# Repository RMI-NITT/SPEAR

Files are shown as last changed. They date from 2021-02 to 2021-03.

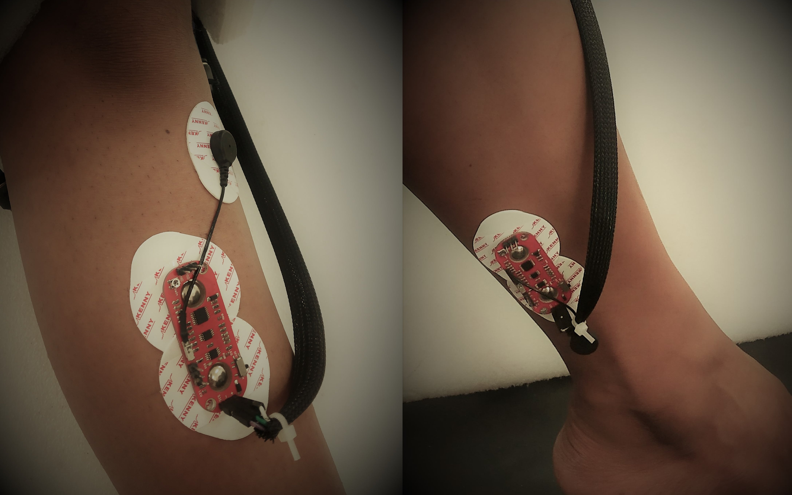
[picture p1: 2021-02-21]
ICC 2019/Latex Pics/Electrodes.jpg

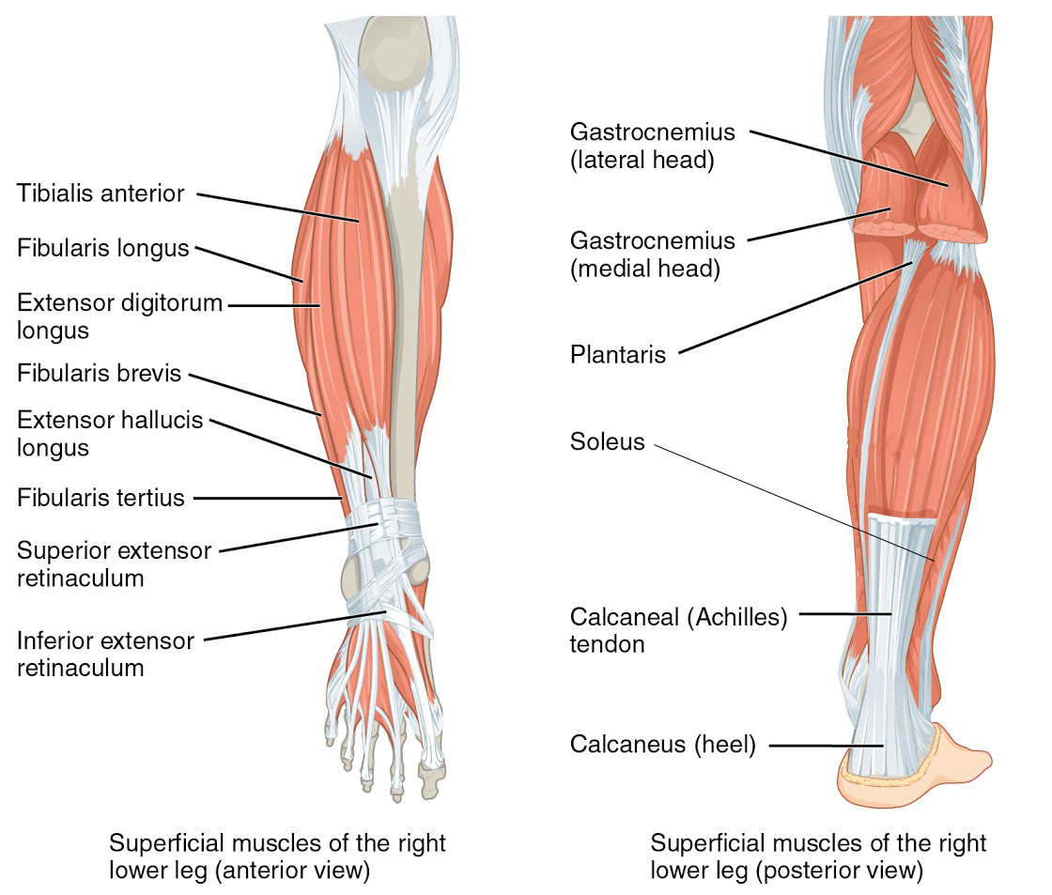
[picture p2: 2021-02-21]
ICC 2019/Latex Pics/Muscles.jpg

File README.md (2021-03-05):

# SPEAR - Soft Pneumatic EMG Assisted Rehabilitation

<p align=justify> SPEAR is an Active Ankle-Foot Orthosis (AFO), aimed at providing an affordable solution for rehabilitating foot drop of stroke survivors.</p>

<p align=justify> Stroke patients often suffer from foot drop, a gait abnormality usually due to the paralysis of the anterior portion muscles of the lower leg, causing an inability or impaired ability to raise the foot at the ankle joint. This leads to extremities of the foot being dragged along the ground while walking, causing tripping and other accidents. Braces or splints that fit into shoes are prescribed to help hold the foot in a normal position. For rehabilitation, most patients are trained to walk with canes, and therapists prescribe physiotherapy for a series of short, intensive sessions. These solutions are expensive and slow processes as they require the presence of skilled personnel and are carried out for short durations.</p>

<p align=justify> The AFO is designed to rehabilitate the foot by augmenting the human musculoskeletal system. It is actuated using McKibben Muscles (Pneumatic Artificial Muscles), which are driven pneumatically. They are cost-effective, lightweight and compliant, offering a significant advantage over Motor Driven orthoses. The orthosis is controlled using Electromyography(EMG) signals from the muscles involved in the motion of the ankle. The EMG sensors are non-invasive, and all computation and control required for the operation of the orthosis run onboard the orthosis in real time.</p>

## Videos
<a href="https://www.youtube.com/watch?v=0MvOgEBvByQ&list=PL44ElmNkyTvBkK0XeyDZ0ApXayw_p0Ibq&index=23">SPEAR Introduction</a>
<br>
<a href="https://www.youtube.com/watch?v=0MvOgEBvByQ&list=PL44ElmNkyTvBkK0XeyDZ0ApXayw_p0Ibq&index=24">SPEAR Working Video</a>
<br>
<a href="https://www.youtube.com/watch?v=SkU-yHnwb48&list=PL44ElmNkyTvCRuWAIcXDtp5S97rujg1kM&index=5">SPEAR Graphical Interface</a>
<br>
<a href="https://www.youtube.com/watch?v=TKFv4CyoDiE&list=PL44ElmNkyTvCRuWAIcXDtp5S97rujg1kM&index=6">SPEAR Project Display</a>

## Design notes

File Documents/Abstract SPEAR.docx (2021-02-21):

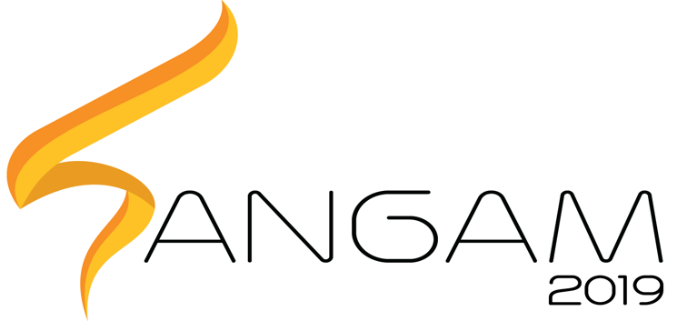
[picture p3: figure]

PRAGYAN HARDWARE HACKATHON

Healthcare and Life Sciences

SPEAR

Soft Pneumatic Electromyographically Assisted Rehabilitation

Name College ID/Roll UG/PG Course/Branch Semester

Name | Roll Number | UG/PG | Branch | Semester
Nitish Gudapati | 111117036 | UG | Mech | III
Koushik Kumaran | 108117056 | UG | ECE | III
Jinesh R | 107117045 | UG | EEE | III
Deepak S V | 107117033 | UG | EEE | III
Himadri Poddar | 110117035 | UG | ICE | III
Mukesh Kanna | 111117070 | UG | Mech | III

1. Project Abstract:

Stroke patients often suffer from Foot Drop, a paralysis of the muscles in the anterior portion of the lower leg, causing an inability or impaired ability to raise the foot from the ankle. This leads to extremities of the foot dragging along the ground while walking, and can cause tripping and other accidents. Presently, patients are trained to walk with canes, and physiotherapy is also prescribed. The physiotherapy requires the presence of a trainer, and these frequent consultations lead to huge expenditure.

Currently, robotic therapeutic tools exist, but the rigidity does not lend itself to the compliant nature of the body, and are unwieldy. They are bulky and heavy which makes them unwearable under regular usage.

As a bio-inspired solution, SPEAR aims to provide a soft robotic approach to the physio therapy. The end effectors at the ankle are a set of soft pneumatic actuators, controlled by electromyographic signals (EMG). This achieves a reduction of weight at the joint, and can be custom made to fit the patient’s needs.

Keywords — Rehabilitative robotics, stroke, foot drop, Soft robotics, soft pneumatic actuators, Electromyography

2. Proposed Design:
A. Objective:

The objective is to rehabilitate patients with foot drop by fabricating a set of soft robotic actuators mimicking the muscle-skeleton system, controlled via electromyography (EMG) signals.

B. Proposed Solution:
  a. Block Diagram:

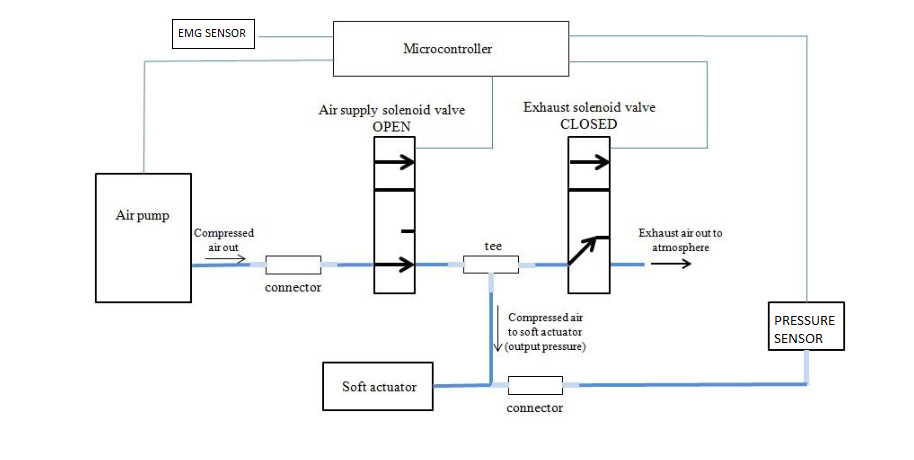
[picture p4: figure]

C. Components Required:

COMPONENTS/PARTS | How is it being used in the proposed solution? Explain its role/functionality.
Thermoplastic Polyurethane / Silicone rubber tube, Nylon Mesh | Fabricate the pneumatic actuator
Air compressor | To compress the air from atmosphere and transfer the compressed air to pneumatic actuators
Solenoid Valve | To control the air flow to pneumatic actuators
MCU | To control the solenoid valve from the data obtained from the corresponding EMG sensors
Electromyographic (EMG) sensor | To measure the electrical activity of muscles

3. Innovativeness of the Proposed Solution

Compared to other rehabilitative robots, a soft robot will be lighter, smaller and wearable. The soft nature of the robot, makes it more compliant with the human body, giving a great increase in comfort over existing solutions. The weight is also much less than that of a rigid structure, reducing the load on the ankle.

Electromyograph signals (EMG) eliminates the need for manual control, and makes the robot feel like a natural extension of the human body.

Compared to traditional therapeutic methods, the cost will be greatly decreased due to the one-time investment.

4. Impact of the proposed solution (Application):

Ease of physiotherapy for those affected with stroke. Physiotherapy is a costly and continuous process, whereas a robotics solution will be a one-time investment. Because of its compliant nature, SPEAR is lighter, smaller and easier to use, contrary to traditional rigid approaches.

5. References

https://softroboticstoolkit.com

https://hpac.harvard.rdu/softrobotics

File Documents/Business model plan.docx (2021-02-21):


PRAGYAN HARDWARE HACKATHON

SPEAR – Soft Pneumatic Electromyography (EMG)

Assisted Rehabilitation

- Key resources: Intellectual: Any patents etc that arise from SPEAR.
- Value propositions: SPEAR offers its customers cost effective, one-time investment solution rather than conventional physiotherapy process which consumes both money and time to a large extent.
- Cost structure:

Orthosis - 6000

EMG Sensors - 5000

McKibben muscles - 400

Compressor and Tank - 1600

Pneumatic Valves - 2500

Miscellaneous (Tubes, connectors, etc.) - 500

Total - 16000

- Future work: Since it is a niche product, SPEAR requires the funding and support of a major healthcare corporation to survive. We plan to present perfect the design and approach specialists from the healthcare industry to acquire funding for production, marketing and distribution of SPEAR.

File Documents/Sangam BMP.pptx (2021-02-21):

## SPEAR Soft Pneumatic EMG Assisted Rehabilitation

Gudapati Nitish
Koushik Kumaran
Mukesh Kanna
Jinesh R
Deepak SV
Himadri Poddar

## Objective:

- The primary objective of SPEAR is to provide a cheap and affordable soft AFO(Ankle-Foot Orthosis) for easy use by patients and reduction of therapy costs.
- SPEAR is designed to be safe due to the use of soft McKibben actuators, eliminating the possibility of injury that is present with any rigid apparatus due to unexpected movement.

## Work Plan:

MONTH | Work completed
December | Actuator Fabrication and testing
January | EMG Signal Processing
February | Orthosis and Tank fabrication
March | Integration of all modules

## Status:

- The orthosis has been fully fabricated with two degrees of freedom (Dorsiflexion and Plantarflexion).
- EMG signal processing has been completed, and user intent has been established.
- A compressor has been fitted with an air tank to provide pressurized air to the orthosis.
- The above three modules have been integrated to give a complete working model.

## Future Work:

The Orthosis can be extended to Inversion and Eversion motion in the ankle.
The Orthosis which has primarily been optimised for rehabilitation can be upgraded to Exoskeleton for the lower limb.
Expandability is present for machine learning algorithms for greater accuracy of EMG intent estimation.
The main features of this exoskeleton:
1. Soft McKibben muscles provide actuation, eliminating rigidity and preventing damage to the user
2. Autonomous control of the Lower limb with Electromyography signals.

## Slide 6

Business Model Plan:

Key Partners Healthcare and Pharmaceutical companies | Key Activities Creation of efficient Supply Chain, Creation of a cheap channel to acquire raw materials. | Value Propositions SPEAR offers its customers cost effective, one-time investment solution rather than conventional physiotherapy process which consumes both money and time to a large extent. | Customer Relationship Dedicated Personal Assistance | Customer Segments Niche market: Patients with foot drop(primarily stroke patients)
| | | Channels Healthcare companies to spread word of mouth to specialists, who can recommend SPEAR to patients
| Key Resources: Intellectual: Any patents, etc. that arise from SPEAR.

Cost Structure: Orthosis- 6000 EMG Sensors - 5000 McKibben muscles – 400 Compressor and Tank – 1600 Pneumatic Valves - 2500 Miscellaneous(Tubes, connectors, etc.) – 500 Total – 16000 | Revenue Streams Funding from Healthcare and Pharmaceutical Companies, Hospitals. Sales Profits

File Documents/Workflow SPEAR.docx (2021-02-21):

S.P.E.A.R Workflow

January:

Week 1:

Fabricator testing

Week 2:

Prototype creation and testing

Week 3:

Pneumatic circuit fabrication, EMG sensor acquisition

Week 4:

Control of Mechanism with hard coded angles, EMG signal processing

February:

Week 1:

EMG signal processing, start of fabrication of orthosis for inversion, eversion

Week 2:

EMG signal processing, completion of orthosis

Week 3:

Completion of EMG signal processing, integration of EMG results with completed orthosis

Week 4:

Testing and refinement

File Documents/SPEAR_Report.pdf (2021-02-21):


## PRAGYAN HARDWARE HACKATHON

## Healthcare and Life Sciences

## SPEAR

## Soft Pneumatic Electromyographically Assisted Rehabilitation

Name | College ID/Roll UG/PG | Course/Branch Semester
Name | Roll Number | UG/PG | Branch | Semester
Nitish Gudapati | 111117036 | UG | Mech | III
Koushik Kumaran | 108117056 | UG | ECE | III
Jinesh R | 107117045 | UG | EEE | III
Deepak S V | 107117033 | UG | EEE | III
Himadri Poddar | 110117035 | UG | ICE | III
Mukesh Kanna | 111117070 | UG | Mech | III

### 1. Project Abstract:

Stroke patients often suffer from Foot Drop, a paralysis of the muscles in the anterior portion of the lower leg, causing an inability or impaired ability to raise the foot from the ankle. This leads to extremities of the foot dragging along the ground while walking, and can cause tripping and other accidents. Presently, patients are trained to walk with canes, and physiotherapy is also prescribed. The physiotherapy requires the presence of a trainer, and these frequent consultations lead to huge expenditure.
Currently, robotic therapeutic tools exist, but the rigidity does not lend itself to the compliant nature of the body, and are unwieldy. They are bulky and heavy which makes them unwearable under regular usage.
As a bio-inspired solution, SPEAR aims to provide a soft robotic approach to the physio therapy. The end effectors at the ankle are a set of soft pneumatic actuators, controlled by electromyographic signals (EMG). This achieves a reduction of weight at the joint, and can be custom made to fit the patient’s needs.

Keywords — Rehabilitative robotics, stroke, foot drop, Soft robotics, soft pneumatic actuators, Electromyography

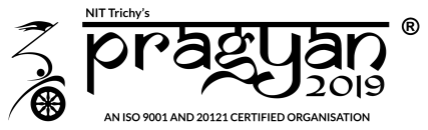
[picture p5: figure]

### 2. Proposed Design:

A. Objective:

The objective is to rehabilitate patients with foot drop by fabricating a set of soft robotic actuators mimicking the muscle-skeleton system, controlled via electromyography (EMG) signals.

B. Proposed Solution:
a. Block Diagram:

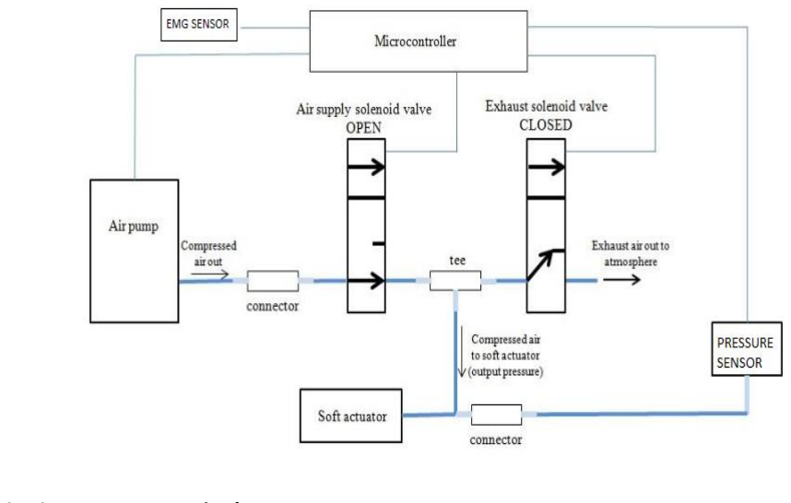
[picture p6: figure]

C. Components Required:
COMPONENTS/PARTS | How is it being used in the proposed solution? Explain its role/functionality.
Thermoplastic Polyurethane / Silicone rubber tube, Nylon Mesh | Fabricate the pneumatic actuator
Air compressor | To compress the air from atmosphere and transfer the compressed air to pneumatic actuators
Solenoid Valve | To control the air flow to pneumatic actuators
MCU | To control the solenoid valve from the data obtained from the corresponding EMG sensors
Electromyographic (EMG) sensor | To measure the electrical activity of muscles

### 3. Innovativeness of the Proposed Solution

Compared to other rehabilitative robots, a soft robot will be lighter, smaller and wearable. The soft nature of the robot, makes it more compliant with the human body, giving a great increase in comfort over existing solutions. The weight is also much less than that of a rigid structure, reducing the load on the ankle.
Electromyograph signals (EMG) eliminates the need for manual control, and makes the robot feel like a natural extension of the human body.
Compared to traditional therapeutic methods, the cost will be greatly decreased due to the one-time investment.

### 4. Impact of the proposed solution (Application):

Ease of physiotherapy for those affected with stroke. Physiotherapy is a costly and continuous process, whereas a robotics solution will be a one-time investment. Because of its compliant nature, SPEAR is lighter, smaller and easier to use, contrary to traditional rigid approaches.

### 5. References

https://softroboticstoolkit.com

https://hpac.harvard.rdu/softrobotics

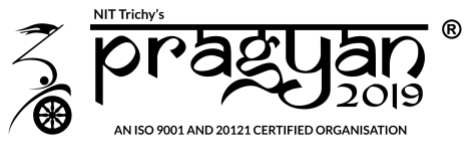
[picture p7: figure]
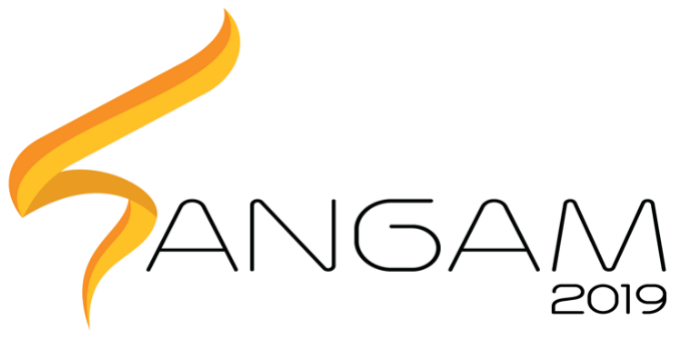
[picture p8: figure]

# Healthcare and Medical Sciences

# S.P.E.A.R

# Soft Pneumatic EMG Assisted Rehabilitation

## PRAGYAN HARDWARE HACKATHON

# Aim

# The objective of S.P.E.A.R is to provide an affordable soft robotic ankle foot orthosis for rehabilitative purposes, aimed primarily

at stroke survivors.

# Application

# Ease of physiotherapy for those affected with stroke. Physiotherapy is a costly and continuous process, whereas a robotics solution will be a one-time investment. Because of its compliant nature, SPEAR is lighter, smaller and easier to use, contrary to traditional rigid

approaches.

# ANKLE MOTION

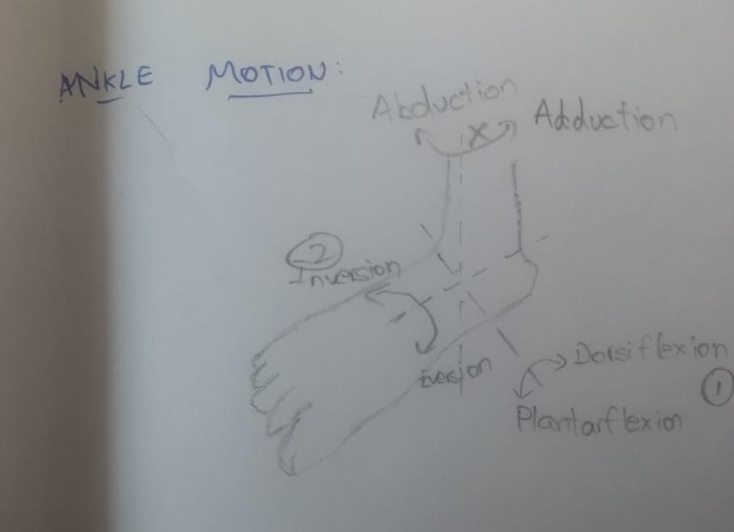
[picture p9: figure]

# Block Diagram

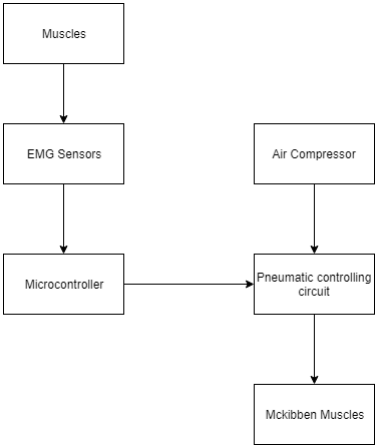
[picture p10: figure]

# Progress Report

# - McKibben Muscles

have been fabricated.

# - The price of a readymade McKibben muscle is minimum

Rs.1500

# - Using off-the shelf components, cost has been reduced to an

average Rs.150,

# depending on Muscle size, diameter

Component | Cost(Rs.)
Bladder(Silicon Rubber) | 40 - 60
Nylon Mesh Sleeve | 40 - 60
Miscellaneous (Connectors, Seals) | 50
Total | 150

# Testing Results

Inner Diameter (inch) | Outer Diameter (inch) | Length (cm) | Slack | Contraction (cm) | Percentage Contraction
1/3 | 1/2 | 20 | No | 2.5 | 12.5
1/3 | 1/2 | 20 | Yes | 0.5 | 2.5
1/2 | 5/8 | 30 | No | 3 | 10

# Muscle Test

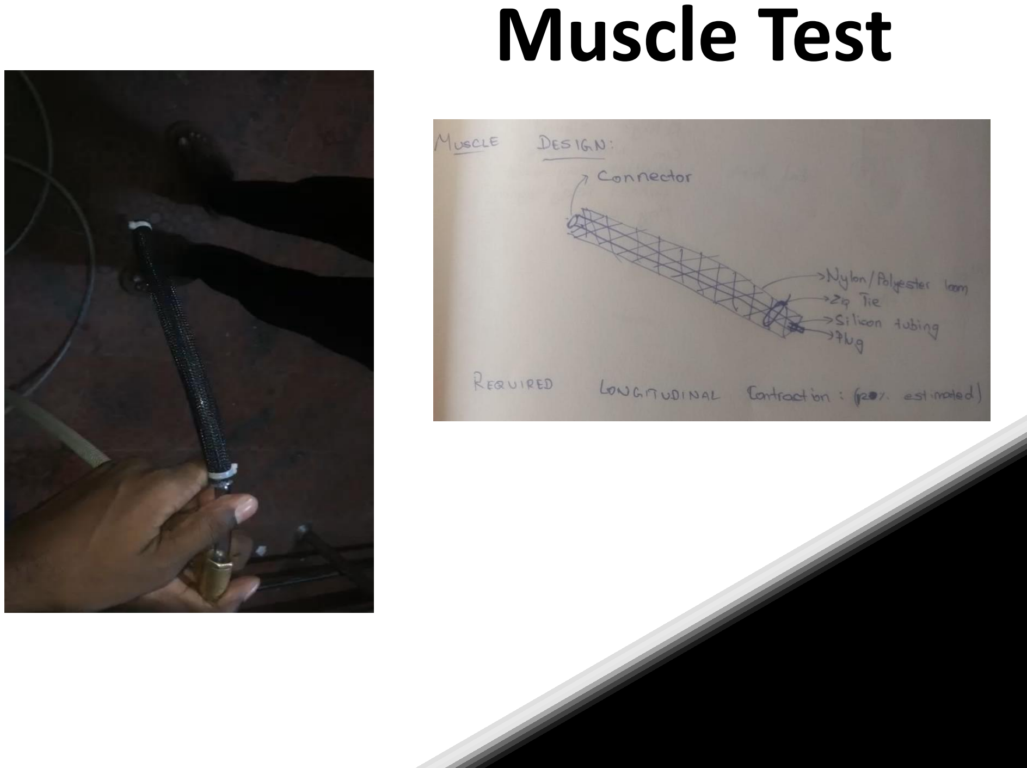
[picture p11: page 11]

# First Prototype

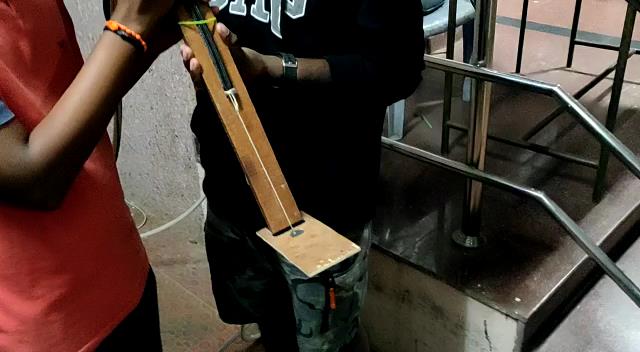
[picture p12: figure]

# Dorsiflexio

n

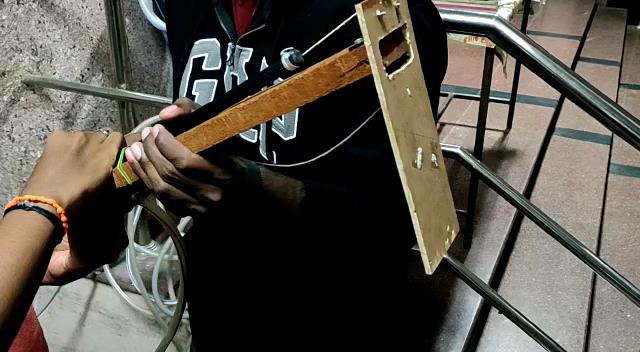
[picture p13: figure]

# Plantarflexion

# Second Prototype (120˚ range of motion)

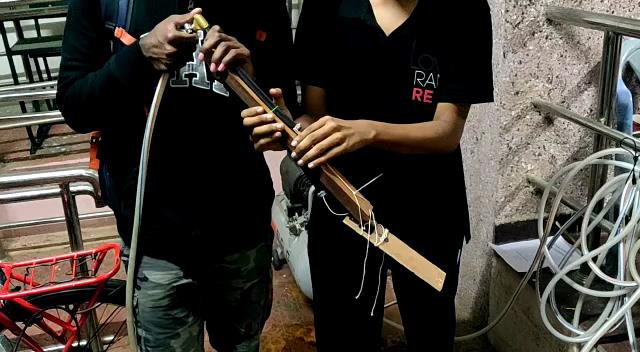
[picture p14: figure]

# Dorsiflexio

n

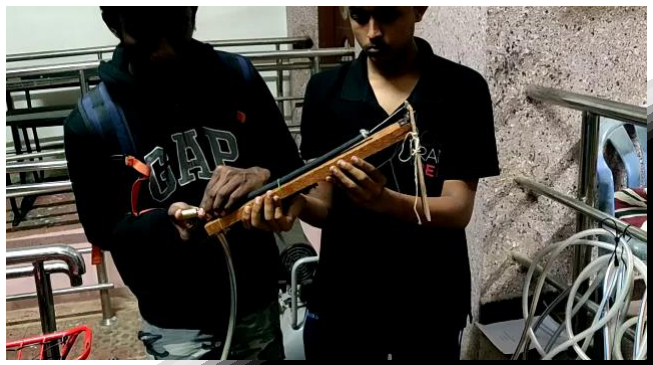
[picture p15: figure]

# Plantarflexion

S.P.E.A.R Workflow

January:

Week 1:

Fabricator testing

Week 2:

Prototype creation and testing

Week 3:

Pneumatic circuit fabrication, EMG sensor acquisition

Week 4:

Control of Mechanism with hard coded angles, EMG signal processing
February:

Week 1:

EMG signal processing, start of fabrication of orthosis for inversion, eversion

Week 2:

EMG signal processing, completion of orthosis

Week 3:

Completion of EMG signal processing, integration of EMG results with completed orthosis

Week 4:

Testing and refinement

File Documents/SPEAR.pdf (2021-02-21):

# S.P.E.A.R

# Soft Pneumatic EMG Assisted Rehabilitation

# Aim

# SPEAR is an Active

Ankle-Foot Orthosis (AFO),

# aimed at providing a cheap and affordable solution for rehabilitating stroke

survivors.

# Abstract

- Stroke patients often suffer from Foot Drop, a paralysis of the muscles in the anterior portion of the lower leg, causing an inability or impaired ability to raise the foot from the ankle. This leads to extremities of the foot dragging along the ground while walking, and can cause tripping and other accidents. Presently, patients are trained to walk with canes, and physiotherapy is also prescribed. The physiotherapy requires the presence of a trainer, and these frequent consultations lead to huge expenditure.
- Currently, robotic therapeutic tools exist, but the rigidity does not lend itself to the compliant nature of the body, and are unwieldy. They are bulky and heavy which makes them unwearable under regular usage.
- As a bio-inspired solution, SPEAR aims to provide a soft robotic approach to the physio therapy. The end effectors at the ankle are a set of soft pneumatic actuators, controlled by electromyography signals (EMG). This achieves a reduction of weight at the joint, and can be custom made to fit the patient’s needs.
- Keywords — Rehabilitative robotics, stroke, foot drop,
Soft | robotics, | soft | pneumatic | actuators,
Electromyography

# Application

## Ease of physiotherapy for those affected with stroke. Physiotherapy is a costly and continuous process, whereas a robotic solution would be a one-time investment. Because of its compliant nature, SPEAR is lighter, smaller and easier to use, contrary to traditional

rigid approaches.

COMPONENTS / PART | Role / Functionality.
Thermoplastic Polyurethane, Nylon Mesh | Fabricate the pneumatic actuator
Air compressor | To compress the air from atmosphere and transfer the compressed air to pneumatic actuators
SolenoidValve | To control the air flow to pneumatic actuators
MCU | To control the solenoid valve from the data obtained from the corresponding EMG sensors
Electromyographic (EMG) sensor | To measure the electrical activity of muscles

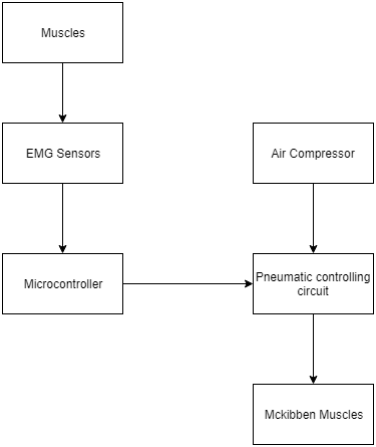
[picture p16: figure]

# Block Diagram

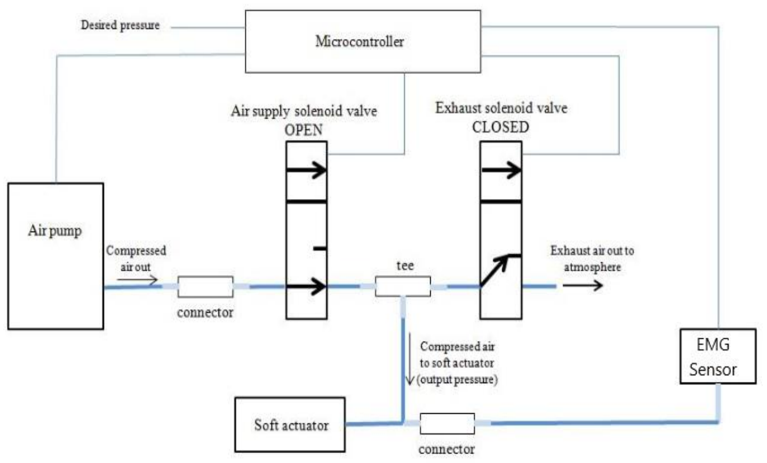
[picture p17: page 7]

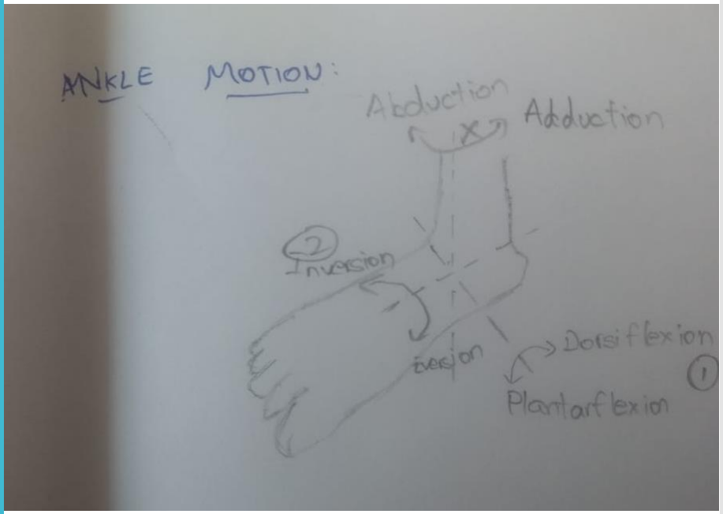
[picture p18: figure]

# Ankle Motion

# McKibben Muscles

## (Soft artificial muscles)

- McKibben Muscles
have been
fabricated.
- The price of a
readymade
McKibben muscle
is minimum
Rs.1500
- Using off-the shelf
components, cost
has been reduced
to an average
Rs.150, depending
on Muscle size,
diameter
Component | Cost(Rs.)
Bladder(Silicon Rubber) | 40 - 60
Nylon Mesh Sleeve | 40 - 60
Miscellaneous (Connectors, Seals) | 50
Total | 150

# Testing Results

Inner Diameter (inch) | Outer Diamete r (inch) | Length (cm) | Slack in Nylon Weave | Contrac tion (cm) | Percent age Contrac tion
1/3 | 1/2 | 20 | No | 2.5 | 12.5
1/3 | 1/2 | 20 | Yes | 0.5 | 2.5
1/2 | 5/8 | 30 | No | 3 | 10

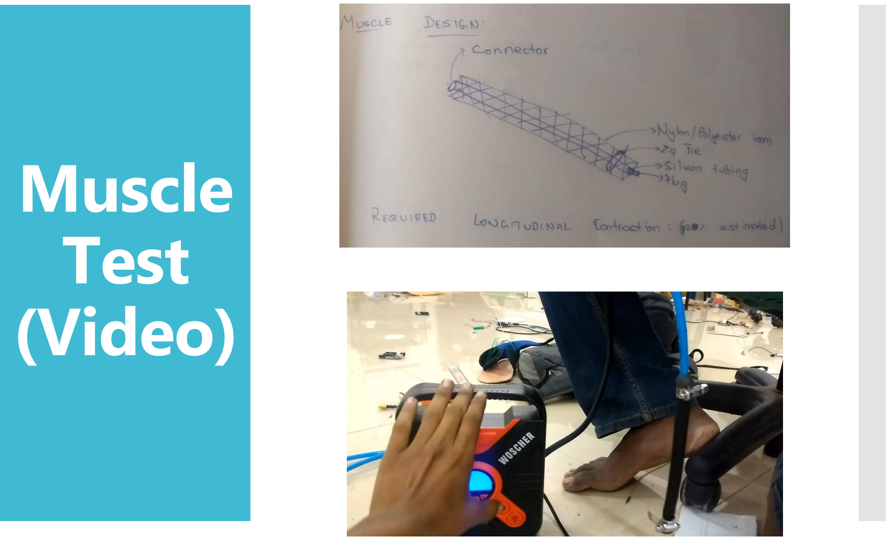
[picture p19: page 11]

# Muscle Test (Video)

# Prototype

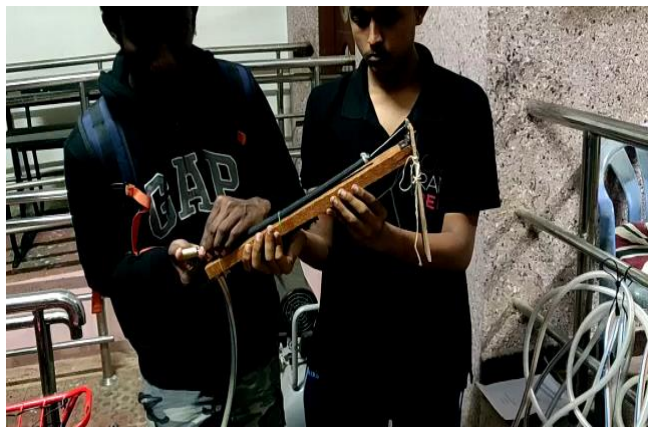
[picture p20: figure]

# (120˚ range of motion)


## Dorsiflexion

## Plantarflexion

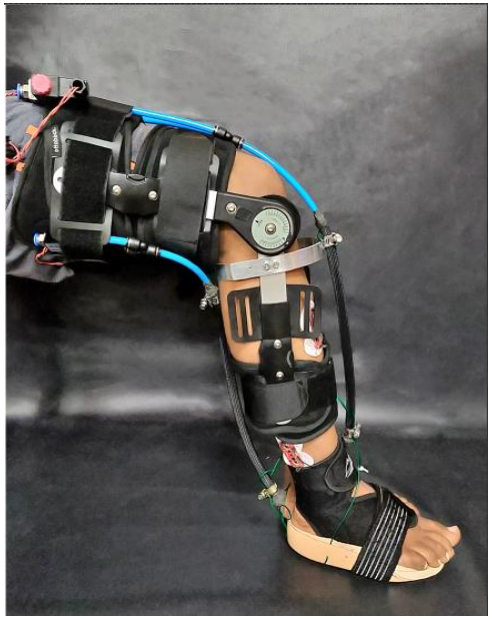
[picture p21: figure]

# Orthosis Design

# EMG Dynamic Thresholding (Video)

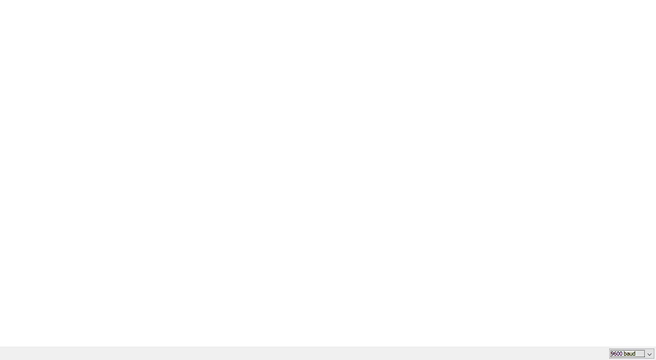
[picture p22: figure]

Tibialis Anterior
for Dorsiflexion

# EMG Voltage-Time Graph

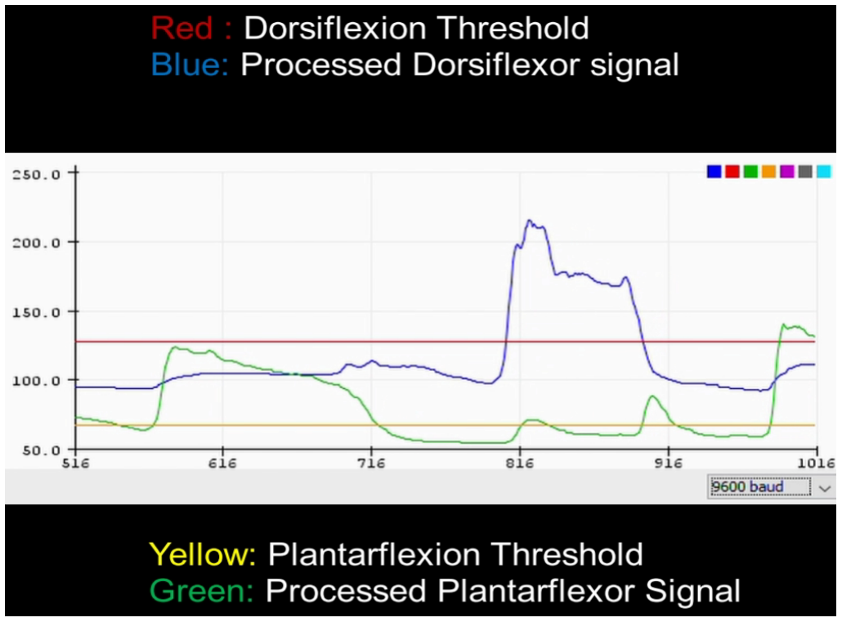
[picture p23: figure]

- Figure shows the voltage time graph obtained after the application of the Kalman Filter to both signals, and the threshold lines calculated using the above formula.

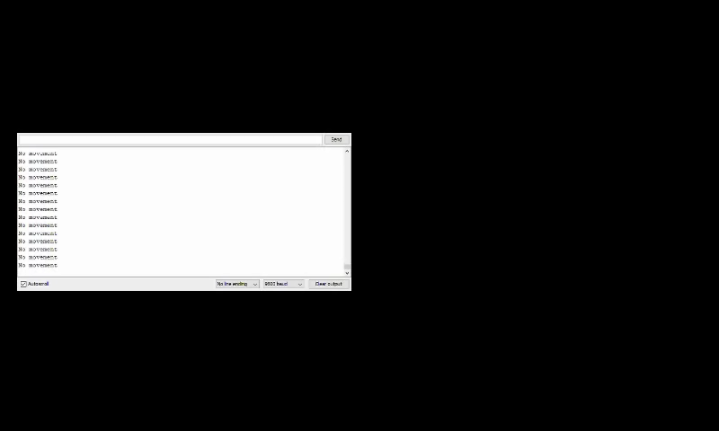
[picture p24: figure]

# EMG Intent Estimation (Video)

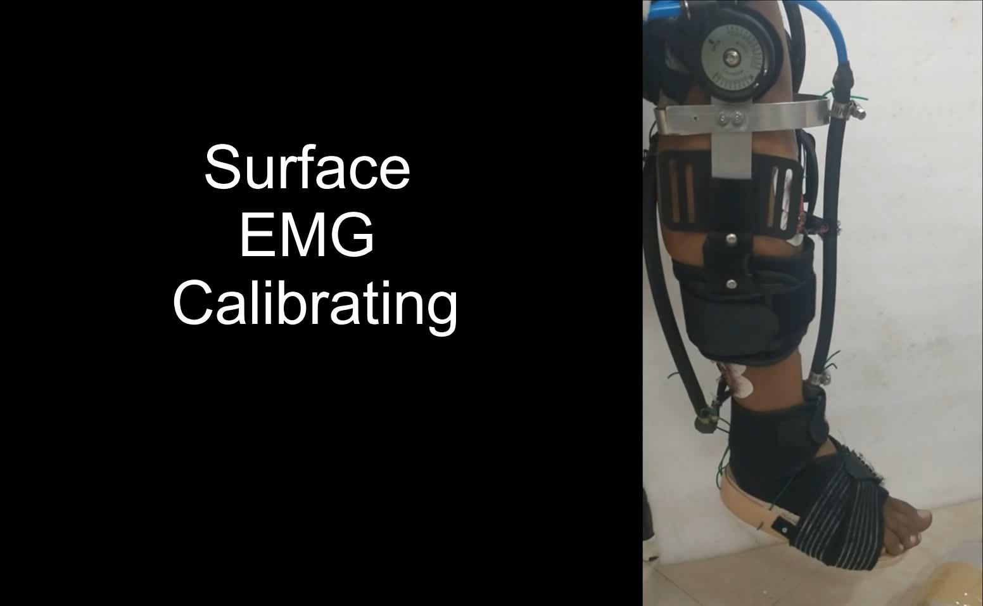
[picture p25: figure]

# Working Video

# Future Work

The Orthosis can be extended to Inversion and Eversion motion in the ankle.
The Orthosis which has primarily been optimised for rehabilitation can be upgraded to Exoskeleton for the lower limb.
Expandability is present for machine learning algorithms for greater accuracy of EMG intent estimation.
The main features of this exoskeleton:
1. Soft McKibben muscles provide actuation, eliminating rigidity and preventing damage to the user
2. Autonomous control of the Lower limb with Electromyography signals.

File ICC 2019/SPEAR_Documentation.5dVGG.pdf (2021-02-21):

## Design and Control of a Low-cost EMG-based Soft Robotic Ankle-Foot Orthosis for Foot Drop Rehabilitation*

Nitish Gudapati¹

, Koushik Kumaran²

, Deepak S V³

, Mukesh Kanna R⁴

, Jinesh R⁵
, Himadri Poddar⁶

Abstract— Stroke patients often suffer from foot drop, a gait abnormality usually due to the paralysis of the anterior portion muscles of the lower leg, causing an inability or impaired ability to raise the foot at the ankle joint. This leads to extremities of the foot being dragged along the ground while walking, causing tripping and other accidents. Braces or splints that fit into shoes are prescribed to help hold the foot in a normal position. For rehabilitation, most patients are trained to walk with canes, and therapists prescribe physiotherapy for a series of short, intensive sessions. These solutions are expensive and slow processes as they require the presence of skilled personnel and are carried out for short durations. In this paper, we present a novel design and control methodology for a 1-DoF Soft Active Ankle-Foot Orthosis (AFO) to address these issues. The AFO is designed to augment the human musculoskeletal system. The AFO is actuated using McKibben Muscles (Pneumatic Artificial Muscles), which are driven pneumatically. They are cost-effective and lightweight, offering a significant advantage over Motor Driven orthoses. The orthosis is controlled using Electromyography(EMG) signals from the muscles involved in the motion of the ankle. The use of EMG signals for control is found to be a better option than existing methods due to its non-invasive nature. It is also found to be simple and cost-effective for intent detection.

Keywords: Active-Foot-Orthosis, Electromyography (EMG), Foot Drop, Rehabilitation, Soft Robotics

I. INTRODUCTION
According to the World Health Organization, 15 million people suffer stroke worldwide each year. Of these, 5 million people die, and another 5 million are permanently disabled [1]. A common ailment for stroke survivors is foot drop, i.e., the inability to actively perform Dorsiflexion the foot. This leads to the occurrence of steppage gait, where the foot drags

*This work was supported by Institute grants through the Robotics and Machine Intelligence Club, NIT Tiruchirappalli, INDIA.
1Nitish Gudapati is a student at the Department of Mechanical Engineering, National Institute of Technology - Tiruchirappalli, Tiruchirappalli, Tamil Nadu 620015, INDIA gudapatinitish9@gmail.com 2Koushik Kumaran is a student at the Department of Electronics and Communication Engineering, National Institute of Technology - Tiruchirappalli, Tiruchirappalli, Tamil Nadu 620015, INDIA koushikkumaran52@gmail.com
3Deepak S V is a student at the Department of Electrical and Electronics Engineering, National Institute of Technology - Tiruchirappalli, Tiruchirappalli, Tamil Nadu 620015, INDIA svdeepak99@gmail.com 4Mukesh Kanna R is a student at the Department of Mechanical Engineering, National Institute of Technology - Tiruchirappalli, Tiruchirappalli, Tamil Nadu 620015, INDIA kanna.r1999@gmail.com
5
Jinesh R S is a student at the Department of Electrical and Electronics Engineering, National Institute of Technology - Tiruchirappalli, Tiruchirappalli, Tamil Nadu 620015, INDIA jineshrs2398@gmail.com 6Himadri Poddar is a student at the Department of Instrumentation and Control Engineering, National Institute of Technology - Tiruchirappalli, Tiruchirappalli, Tamil Nadu 620015, INDIA himadripoddar.nitt@gmail.com

along, requiring the patient to raise their knee higher than usual in the swing phase to counter this [2]. The patient’s foot slaps the ground during the foot strike phase of the gait cycle. Studies have shown that the entire kinematic chain of the lower body is disturbed, resulting in the functioning of the motor system under abnormal load [3].
Patients generally undergo therapy to regain motor control, and the required recovery can take from months to years to complete as shown in Fig.1 [4]. The available number of medical professionals are far less than the requirement, and they may not be accessible to all those who need it [5]. To this end, robotic devices can significantly decrease the burden on therapists and caregivers and can be used to provide intensive task-oriented practice.

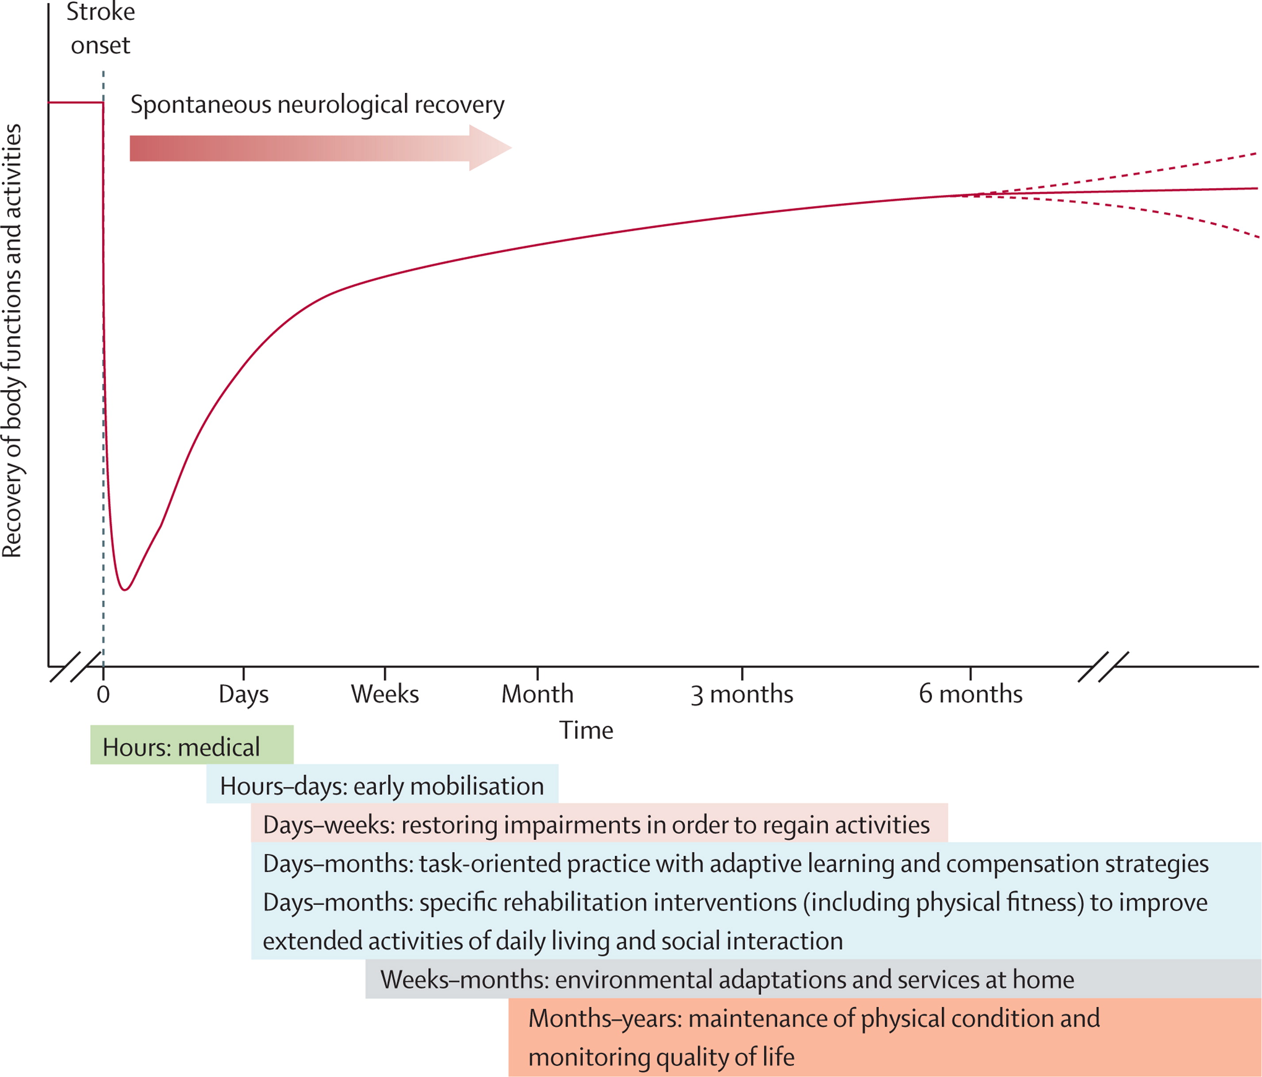
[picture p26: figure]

Fig. 1. A hypothetical pattern of recovery after stroke with the timing of intervention strategies Source: [4]

Considerable research has gone into developing such robotic devices, especially for upper-body rehabilitation [6]
[7] [8]. Most of these devices, however, are rigid, heavy and unwieldy. In recent years, the interest in a compliant robotic system has increased exponentially, due to the significant advantages they provide. Mckibben muscles or Pneumatic Artificial Muscles (PAM) are a possible actuation method with properties that make them uniquely suited for the application presented. These properties are explored in depth in Section IV.
In this paper, we describe the design and control of a single DOF orthosis, actuated with PAMs and controlled with Electromyography(EMG) Signals. The EMG sensors are non-invasive, and all computation and control required for the operation of the orthosis runs onboard the orthosis in real time. The design is compliant, lightweight and wearable. Section II explains the practices and techniques involved in the rehabilitation of the foot and section III explains the existing orthoses and exoskeletons for foot rehabilitation. Section IV discusses the construction and working of the prototype, and the results are presented in section V. Some concluding remarks and future scope is mentioned in section VI.

II. REHABILITATION TECHNIQUES

To understand the requirements and specifications of stroke rehabilitation devices, a brief introduction of existing techniques is given below [9].

A. Physiotherapy
The primary technique used is Physiotherapy which involves assessment of a Physiotherapist using various techniques. The techniques include various exercises.
1) Mobility training: To stabilise and strengthen to enhance balance and support.
2) Range of motion therapy: Helps in easing muscle tension allowing a good range of motion.
B. Technology-assisted
1) Functional electrical stimulation: This method involves inducing contraction to the weak muscles by application of electricity which helps in training them.
2) Game system technology: It is based on the idea of integration of games for rehabilitation. They involve functional activities and keep the patient occupied and motivated with games during the rehabilitation process.

III. EXISTING TECHNOLOGIES FOR REHABILITATION

Robotic exoskeletons have been employed in assisting individuals suffering from physical disability either for the advancement of therapy or as a permanent assistive tool. They are of various types, and can be classified based on their method of actuation:
- Rigid actuation: These devices are actuated using DC motors, Steppers etc.
- Soft actuation: These devices are actuated using compliant methods and are generally actuated pneumatically or using shape memory alloy (SMA) [10][13][14][15]. The AFO described in this paper falls under this category.
A. Rigid Actuation
1) Anklebot at Massachusetts Institute of Technology (MIT), USA: The Anklebot is a 3-DOF wearable robot, which is actuated by two linear screw actuators using two brushless dc motors. The linear actuators are mounted in parallel and provide actuation in two of the ankles 3-DOF, namely dorsiflexion-plantarflexion and inversioneversion [11]. Position information is provided by two sets of sensors: rotary encoders and linear encoders. No input is given by the user, and all movement is externally decided.
2) ALEX at University of Delaware, USA: This exoskeleton is mounted with a walker to support the device. The controller applies a force-field at the ankle of the subject. The linear actuators are mounted at the hip and knee of the orthosis. The torque generated by the actuators at these joints simulate the tangential forces needed to move the ankle of the subject along the trajectory [12]. The disadvantage is that it is not easily portable.
B. Soft Actuation
1) Wearable Soft Exoskeleton at Carnegie Mellon University, USA: The exoskeleton uses four PAMs placed on one of the lower legs (three anterior muscles for dorsiflexion, inversion, and eversion, and one posterior muscle for plantarflexion), which is connected to the knee brace and the foot brace with the help of artificial tendons. The artificial muscles were designed and placed as counterparts close to the biological muscles so that the device could provide additional forces to the corresponding muscles [13]. It is externally controlled using solenoid valves, and the sensors are used as position feedback for control without getting any input from the user. It helps with therapy, but it does not provide much independence for the user.
2) Powered ankle foot orthosis at University of Michigan, USA: This orthosis is actuated by PAMs providing only plantar flexion torque. It uses a real-time computer interface for controlling the air pressure supplied to the PAMs. The pressure is determined based on foot contact with the ground using a footswitch which is placed under the foot [14].
3) Adaptive control of actuated ankle foot orthosis (AAFO) at Paris-Est Crteil University, France: AAFO uses a predetermined trajectory of the ankles swing phase of the gait cycle, which helps in controlling the amount of assistance required for the ankle-foot orthosis. This method is employed as the current technologies are based on human/robot parameters, which are to be identified to set the magnitude of assistance required [15].

IV. CONSTRUCTION AND WORKING

A. Design of the Prototype

The design of the AFO focuses on achieving the following goals:
- User Comfort
- Minimal weight.
- Complete Range of Motion in a single axis.
- Simple setup.
- Minimal cost
1) Pneumatic Artificial Muscle Design: Each PAM consists of a silicone rubber tube, placed within a nylon mesh sleeve. The sleeve is kept in place with hose clamps on either end. One end is pneumatically sealed, and the other end is used as an inlet for pressurised air. Air is let in at around 40 psi. When air flows into the tube, it tends to expand volumetrically. The sleeves structure does not allow it to expand longitudinally, and rather, it expands radially while contracting longitudinally.

Multiple studies have been performed on these PAMs, and find the force-length characteristics to be similar to that of a muscle [16]. The materials used in the PAM are compliant, lightweight and low-cost. These properties make PAMs well suited for the AFO.

The required length and diameter of the PAMs were decided upon through experiments with various configurations, presented in Section V.


Fig. 2. AFOs Layout. Components labelled from (1) to (11): (1) Arduino Uno; (2) Motor drivers; (3) Solenoid Valves; (4) Li-Po; (5) Panel for electronic circuitry; (6) Knee braces; (7) PAM Mount; (8) PAM; (9) Foam padding; (10) Adjustable strings; (11) Orthotic Sole

2) Orthosis Design: The ground link of the Orthosis is located above the knee and functions and is connected to the second link around via a hinge joint. Another link is positioned on foot and acts as the end effector.

The brace and the sole are connected using two PAMs in an agonist-antagonist configuration, each one providing the necessary Dorsiflexion and Plantarflexion forces respectively. They can be modelled as slider mechanisms. The placement of the PAMs on the end is dependant on the required actuation torque and range of motion. Since PAMs are shown to provide a good amount of force [16], but only limited contraction, the choice was made to place them very close to the joint. This allows the AFO to achieve the entire Range of Motion which is roughly 20 degrees for dorsiflexion and 50 degrees for plantarflexion [17].

Some similar devices [18][19] have been constructed with the ground at the shin, connected to the ankle end effector in a similar fashion. We found that in this configuration, the transverse reaction forces during PAM contraction resulted in skin deformation at the skin-AFO interface. Such deformation was found to cause user discomfort and restrict the range of motion of the AFO. By placing the ground above the knee, the vector of reaction force is made almost completely normal to the skin-AFO interface as shown in Fig. 3.


Fig. 3. Interface between the skin and the orthosis


Fig. 4. Pneumatic Circuit

3) Electronics and Pneumatic Circuitry: Each PAM is controlled by a pair of 12V DC 2-Position 2-Way Solenoid Valves, where one acts as an inlet and the other acts as an outlet. Each pair of valves is connected to an L298N driver for logic. The drivers are connected to a Microcontroller Unit(MCU) (Arduino UNO). Two Myoware EMG sensors from Advancer Technologies are connected to the same MCU. The entire setup is powered by a 12V Lithium-Polymer Battery and placed on the ground link to optimise weight distribution throughout the AFO.
Both the inlet valves are connected to an air tank with pressurised air at 60psi, and the exhaust valves are left open to the atmosphere as shown in Fig.4. All pneumatic connections were made with 8 mm OD x 6 mm OD Polyurethane Pneumatic Tubes. The control methodologies for the PAMs are described in Section IV.B.4.
B. Control of the Orthosis
1) Signal Acquisition: In order to detect the intent of the user, the AFO uses EMG electrodes, connected to an MCU. Each McKibben muscle is placed so as to assist the functioning of a specific muscle. The targeted muscles are:
- Tibialis Anterior for Dorsiflexion
- Soleus for Plantarflexion
The positions of these muscles are depicted in Fig.5.
Each muscle requires a single non-invasive EMG sensor. Each sensor requires the placement of three electrodes to capture the differential component of the signal travelling across the muscle. As per EMG electrode placement standards [20], one electrode is placed near the centre of a muscle, one electrode near the end of a muscle and a ground electrode is placed near a bone for reference.


Fig. 5. Muscles of the leg Source: [21]

The rectified and integrated signal is passed from the signal pin of the sensor in the form of a 0 to 3.3V analog wave which is sampled by the 10-bit ADC of the MCU at a rate of 200Hz.


Fig. 6. Left: Electrode placement over the Tibialis Anterior Muscle; Right: Electrode placement over the Soleus Muscle

2) EMG Analysis: The rectified and integrated signals(signal envelopes) from the MyoWare muscle sensors were erratic and caused sudden spikes in the signal. To overcome this, the signals from both EMG sensors were passed to two independent 1-dimensional Kalman Filters, and the filtered output values of each iteration were taken as the estimated values for the next iteration. It was found that a Kalman Gain of 0.001 for both the filters gave the best results in removing noise from the signals, by inducing negligible latency in the filtered output as shown in Fig. 7. EMG signals for a muscle are highly dependant on a multitude of factors such as electrode placement, fatigue, and the physical and mental state of the user [22][23]. Hence, calibration is required before every session. This happens automatically on initialisation of the AFO. This calibration procedure sets the threshold for each muscle to enable intent estimation, which is described below.
The rest state characteristics of each muscle are obtained by recording the unfiltered EMG envelope for 10 seconds. The mean (µrest) and standard deviation (σrest) of this data


Fig. 7. EMG Signal Acquision, Filtering and Thresholding


Fig. 8. Intent Detection

are extracted from this data. Using the collected data, a threshold is calculated for each target muscle using (1) for Dorsiflexion and (2) for Plantarflexion. This threshold is then used to detect activation of each muscle. The muscle is found to be actively contracting when the filtered signal exceeds the threshold.
For Tibialis Anterior muscle, the threshold is determined by Eqn.1,
T = µrest +3σrest | (1)

For Soleus muscle, the threshold is determined by Eqn.2,

T = µrest +8σrest | (2)

Studies have shown that a threshold equal to the mean added to a multiple of the standard deviation gives good results when applied to the EMG envelope [24]. The values of the constant multiplier for standard deviation were determined experimentally, and the results of these tests are described in Section V.
3) Intent Detection Logic: Using the described method, it is possible to determine the state of a muscle in real time. Through experiments, it was found that the Soleus muscle was active during Plantarflexion and the initial, final stages of Dorsiflexion. This is visualized in Fig. 13, in which the patient performed Plantarflexion, followed by Dorsiflexion. Using this information, the User Intent can be detected by the method specified in Fig. 8

4) Control of PAM with EMG: The user closes the feedback loop by attempting to move their ankle by muscle contraction. This eliminates the need of external feedback, and allows real time intent detection.


Fig. 9. Operation Flowchart

In order to contract a PAM, pressurised air is inflated into it by opening the inlet valve and by closing the outlet valve. In order to relax (expand) a PAM, the air inside it is exhausted by closing the inlet valve and opening the outlet valve. The below table summarises the valve positions for different PAM configurations.

TABLE I

STATE OF SOLENOID VALVES

PAM movement | Inlet Valve | Exhaust Valve
Relax (Deflate) | Close | Open
Contract (Inflate) | Open | Close

In order to ensure smooth movement of the patients foot and avoid sudden movement, the speed of inflation/deflation of the PAMs was reduced by applying a Pulse Width Modulated(PWM) signal to the valves as shown in Fig. 10 and Fig.
11. Through experiments, it was found that a PWM signal with a time period of half a second and a duty cycle of 10% for 5 seconds was ideal.


Fig. 10. PWM Timing diagram during Inflation of the Muscle


Fig. 11. PWM Timing diagram during Exhaust of the Muscle

After detecting user intent, control signals from the MCU are sent to the pneumatic valves through the motor drivers. Table II describes the state of each PAM with respect to various user inputs.

TABLE II

STATE OF PNEUMATIC ARTIFICIAL MUSCLES

Intent | Dorsiflexor PAM | Plantarflexor PAM
Rest State | Relax | Relax
Plantarflexion | Relax | Contract
Dorsiflexion | Contract | Relax
V. RESULTS AND STATISTICAL DATA


Fig. 12. Prototype of the Ankle-Foot-Orthosis

A. Pneumatic Artificial Muscles Tests
The PAMs were tested by inflation at 35 psi with no external load to select the ideal contraction length required for the AFO.

TABLE III
PAM TESTS
Inner Diameter (inches) | Outer Diameter (inches) | Length of muscle (cm) | Length Contraction (cm) | Percentage Contraction (%)
1/3 | 1/2 | 20 | 2.5 | 12.5
1/2 | 5/8 | 20 | 1.8 | 9
1/3 | 1/2 | 30 | 5.1 | 17
1/2 | 5/8 | 30 | 3 | 10
B. EMG control Tests
The AFO was tested by three healthy individuals in two sessions each. The patients were asked to Flex their legs in a particular direction multiple times, and the percentage accuracy of intent detection was calculated.

TABLE IV

SESSION 1: SUBJECTS WERE WELL RESTED

Subject | Dorsiflexion Accuracy(%) | Plantarflexion accuracy(%)
1 | 95 | 95
2 | 100 | 90
3 | 95 | 90

TABLE V

SESSION 2: SUBJECTS WERE FATIGUED

Subject | Dorsiflexion Accuracy(%) | Plantarflexion accuracy(%)
1 | 95 | 90
2 | 90 | 90
3 | 90 | 90

From the above results, it is found that the simple control scheme presented is able to achieve a mean Dorsiflexion accuracy of 94.17%, and inaccuracies being 4.17% true-negative and 1.66% false-positive and. The mean Plantarflexion accuracy is 90.83% and the inaccuracies are 5.83% true-negative and 3.34% false-positive. It is worth noting that the accuracy decreases minimally when the patients are not wellrested. For well rested patients, the control scheme achieves a mean Dorsiflexor accuracy of 96.7% and inaccuracies being 1.65% false-positive and 1.65% true-negative. The mean Plantarflexion accuracy is 91.7% and the inaccuracies are 6.7% true-negative and 1.6% false-positive.


Fig. 13. Voltage-time graph obtained after the application of the Kalman Filter to both signals as well as the threshold lines

VI. CONCLUSIONS
The design and control of a 1 DOF Soft Ankle Foot Orthosis has been presented in this paper. The prototype shows promise to be as a therapeutic alternative. The AFO uses EMG signals which are reliable and easy to calibrate. The main purpose of the work is to replace the rigid and heavy hardware previously used for robotic rehabilitation. The AFO uses McKibben Muscles/PAMs, which are pneumatically actuated, low-cost and lightweight. The torque provided by the AFO can be increased by enhancing air pressure driving techniques, and this could allow the use of the device as a powered exoskeleton. Also, machine learning algorithms could be used to estimate the intent of the user with greater accuracy. The device could also be further developed by incorporating more degrees of freedom. This would allow the AFO to perform Inversion and Eversion of the leg.
| REFERENCES
[1] ”World Health Report” - 2002 from the World Health Organization Retrieved on: 10 May 2019 from http://www.who.int/whr/2002/en/.
[2] ”Walking abnormalities” MedlinePlus Retrieved on: 5 June 2019 from https://medlineplus.gov/ency/article/003199.htm
[3] Wiszomirska I, Bakiewicz M, Kaczmarczyk K, Brzuszkiewicz-Kumicka G, Wit A. Effect of Drop Foot on Spatiotemporal, Kinematic, and Kinetic Parameters during Gait. Appl Bionics Biomech. 2017;2017:3595461. doi:10.1155/2017/3595461.
[4] P. Langhorne, J. Bernhardt and G. Kwakkel, Stroke Rehabilitation, Stroke Care 2, The Lancet Vol 377, May 2011.
[5] K.X. Khor, H.A. Rahman, S.K. Fu et al. A Novel Hybrid Rehabilitation Robot for Upper and Lower Limbs Rehabilitation Training. Int. Conf. on Robot PRIDE (ConfPRIDE) 2013-2014, Procedia Computer Science 42 (2014) p. 293-300.
[6] A. Asokan and M. Vigneshwar, ”Design and Control of an EMG-based Low-cost Exoskeleton for Stroke Rehabilitation,” 2019 Fifth Indian Control Conference (ICC), New Delhi, India, 2019, pp. 478-483. doi: 10.1109/INDIANCC.2019.8715555
[7] Kim B, Deshpande AD. An Upper-Body Rehabilitation Exoskeleton Harmony with an Anatomical Shoulder Mechanism: Design, Modeling, Control, and Performance Evaluation. Int. Journal. of Robotics Research (IJRR) 2017, Vol 36 Issue 4, p. 414-435.
[8] J. C. Perry and J. Rosen.Design of a 7 Degree-of-Freedom Upper-Limb Powered Exoskeleton. The First IEEE/RAS-EMBS Int. Conf. on Biomedical Robotics and Biomechatronics, 2006. BioRob 2006., Pisa, 2006, pp. 805-810.
[9] | Stroke | rehabilitation: | What | to | expect | as | you | recover.
(May | 24, | 2017). | Retrieved | on | 2 | June | 2019, | from
https://www.mayoclinic.org/diseasesconditions/stroke/in-depth/strokerehabilitation/art-20045172
[10] K. Ikuta, ”Micro/miniature shape memory alloy actuator,” Proceedings., IEEE International Conference on Robotics and Automation, Cincinnati, OH, USA, 1990, pp. 2156-2161 vol.3. doi: 10.1109/ROBOT.1990.126323
[11] Roy, A., Krebs, H. I., Williams, D. J., Bever, C. T., Forrester, L. W., Macko, R. M., & Hogan, N. (2009). Robot-Aided Neurorehabilitation: A Novel Robot for Ankle Rehabilitation. IEEE Transactions on Robotics, 25(3), 569582. doi:10.1109/tro.2009.2019783
[12] Banala, S. K., Seok Hun Kim, Agrawal, S. K., & Scholz, J. P. (2009). Robot Assisted Gait Training With Active Leg Exoskeleton (ALEX). IEEE Transactions on Neural Systems and Rehabilitation Engineering, 17(1), 28.doi:10.1109/tnsre.2008.2008280
[13] Park, Y.-L., Chen, B., Prez-Arancibia, N. O., Young, D., Stirling, L., Wood, R. J., Nagpal, R. (2014). Design and control of a bio-inspired soft wearable robotic device for anklefoot rehabilitation. Bioinspiration & Biomimetics, 9(1), 016007.doi:10.1088/1748-3182/9/1/016007
[14] Gordon, K. E., Sawicki, G. S., & Ferris, D. P. (2006). Mechanical performance of artificial pneumatic muscles to power an anklefoot orthosis. Journal of Biomechanics, 39(10), 18321841.doi:10.1016/j.jbiomech.2005.05.018
[15] Arnez-Paniagua, V., Rifai, H., Amirat, Y., & Mohammed, S. (2017). Adaptive control of an actuated-ankle-foot-orthosis. 2017 International Conference on Rehabilitation Robotics (ICORR). doi:10.1109/icorr.2017.8009474
[16] Takosoglu, Jakub & Laski, P & Blasiak, Slawomir & Bracha, Gabriel & Pietrala, Dawid. (2016). Determining the Static Characteristics of Pneumatic Muscles. Measurement and Control. 49. 62-71. 10.1177/0020294016629176.
[17] ”Generally Accepted Values for Normal Range of Motion (ROM) in Joints” (May 14, 2019) Retrieved on 8 June 2019 from https://www.verywellhealth.com/what-is-normal-range-of-motion-ina-joint-3120361
[18] Ferris DP, Czerniecki JM, Hannaford B. An ankle-foot orthosis powered by artificial pneumatic muscles. J Appl Biomech. 2005;21(2):189197.
[19] Zhu, Y. (2017). Design and web-based control of a soft ankle foot orthosis. 17. 82-88.
[20] Datasheet Retrieved on 8 June 2019 from https://cdn.sparkfun.com/datasheets/Sensors/Biometric/MyowareUserManualAT-04-001.pdf
[21] ”Appendicular | Muscles | of | the | Pelvic | Girdle | and
Lower | Limbs” | Retrieved | on | 8 | July | 2019 | from
https://cnx.org/contents/FPtK1zmh@8.108:y9 gDy74@5/Appendicular-Muscles-of-the-Pelvic-Girdle-and-Lower-Limbs
[22] Jamal, Muhammad. (2012). Signal Acquisition Using Surface EMG and Circuit Design Considerations for Robotic Prosthesis. Computational Intelligence in Electromyography Analysis - A Perspective on Current Applications and Future Challenges. 10.5772/52556.
[23] M. B. I. Reaz, M. S. Hussain, F. Mohd-Yasin. Techniques of EMG signal analysis: detection, processing, classification and applications. Biol. Proced. Online 2006; 8(1): 11-35.
[24] K. T. O zgunen, U. C elik, S. S. Kurdak. Determination of an optimal threshold value for muscle activity detection in EMG analysis. Journal of Sports Science and Medicine (2010) 9, pp. 620-628.

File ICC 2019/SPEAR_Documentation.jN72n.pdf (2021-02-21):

72 pt
1 in
25.4 mm


54 pt
0.75 in
19.1 mm

54 pt
0.75 in
19.1 mm

0.75 in
19.1 mm

Margin requirements for first page Paper size this page US Letter

## Design and Control of a Low-cost EMG-based Soft Robotic Ankle-Foot Orthosis for Foot Drop Rehabilitation*

Nitish Gudapati¹

, Koushik Kumaran²

, Deepak S V³

, Mukesh Kanna R⁴

, Jinesh R⁵
, Himadri Poddar⁶

Abstract— Stroke patients often suffer from foot drop, a gait abnormality usually due to the paralysis of the anterior portion muscles of the lower leg, causing an inability or impaired ability to raise the foot at the ankle joint. This leads to extremities of the foot being dragged along the ground while walking, causing tripping and other accidents. Braces or splints that fit into shoes are prescribed to help hold the foot in a normal position. For rehabilitation, most patients are trained to walk with canes, and therapists prescribe physiotherapy for a series of short, intensive sessions. These solutions are expensive and slow processes as they require the presence of skilled personnel and are carried out for short durations. In this paper, we present a novel design and control methodology for a 1-DoF Soft Active Ankle-Foot Orthosis (AFO) to address these issues. The AFO is designed to augment the human musculoskeletal system. The AFO is actuated using McKibben Muscles (Pneumatic Artificial Muscles), which are driven pneumatically. They are cost-effective and lightweight, offering a significant advantage over Motor Driven orthoses. The orthosis is controlled using Electromyography(EMG) signals from the muscles involved in the motion of the ankle. The use of EMG signals for control is found to be a better option than existing methods due to its non-invasive nature. It is also found to be simple and cost-effective for intent detection.

Keywords: Active-Foot-Orthosis, Electromyography (EMG), Foot Drop, Rehabilitation, Soft Robotics

I. INTRODUCTION
According to the World Health Organization, 15 million people suffer stroke worldwide each year. Of these, 5 million people die, and another 5 million are permanently disabled [1]. A common ailment for stroke survivors is foot drop, i.e., the inability to actively perform Dorsiflexion the foot. This leads to the occurrence of steppage gait, where the foot drags

*This work was supported by Institute grants through the Robotics and Machine Intelligence Club, NIT Tiruchirappalli, INDIA.
1Nitish Gudapati is a student at the Department of Mechanical Engineering, National Institute of Technology - Tiruchirappalli, Tiruchirappalli, Tamil Nadu 620015, INDIA gudapatinitish9@gmail.com 2Koushik Kumaran is a student at the Department of Electronics and Communication Engineering, National Institute of Technology - Tiruchirappalli, Tiruchirappalli, Tamil Nadu 620015, INDIA koushikkumaran52@gmail.com
3Deepak S V is a student at the Department of Electrical and Electronics Engineering, National Institute of Technology - Tiruchirappalli, Tiruchirappalli, Tamil Nadu 620015, INDIA svdeepak99@gmail.com 4Mukesh Kanna R is a student at the Department of Mechanical Engineering, National Institute of Technology - Tiruchirappalli, Tiruchirappalli, Tamil Nadu 620015, INDIA kanna.r1999@gmail.com
5
Jinesh R S is a student at the Department of Electrical and Electronics Engineering, National Institute of Technology - Tiruchirappalli, Tiruchirappalli, Tamil Nadu 620015, INDIA jineshrs2398@gmail.com 6Himadri Poddar is a student at the Department of Instrumentation and Control Engineering, National Institute of Technology - Tiruchirappalli, Tiruchirappalli, Tamil Nadu 620015, INDIA himadripoddar.nitt@gmail.com

along, requiring the patient to raise their knee higher than usual in the swing phase to counter this [2]. The patient’s foot slaps the ground during the foot strike phase of the gait cycle. Studies have shown that the entire kinematic chain of the lower body is disturbed, resulting in the functioning of the motor system under abnormal load [3].
Patients generally undergo therapy to regain motor control, and the required recovery can take from months to years to complete as shown in Fig.1 [4]. The available number of medical professionals are far less than the requirement, and they may not be accessible to all those who need it [5]. To this end, robotic devices can significantly decrease the burden on therapists and caregivers and can be used to provide intensive task-oriented practice.

Fig. 1. A hypothetical pattern of recovery after stroke with the timing of intervention strategies Source: [4]

Considerable research has gone into developing such robotic devices, especially for upper-body rehabilitation [6]
[7] [8]. Most of these devices, however, are rigid, heavy and unwieldy. In recent years, the interest in a compliant robotic system has increased exponentially, due to the significant advantages they provide. Mckibben muscles or Pneumatic Artificial Muscles (PAM) are a possible actuation method with properties that make them uniquely suited for the application presented. These properties are explored in depth in Section IV.
In this paper, we describe the design and control of a single DOF orthosis, actuated with PAMs and controlled with Electromyography(EMG) Signals. The EMG sensors

54 pt
0.75 in
19.1 mm

54 pt
0.75 in
19.1 mm

Margin requirements for the other pages

are non-invasive, and all computation and control required for the operation of the orthosis runs onboard the orthosis in real time. The design is compliant, lightweight and wearable. Section II explains the practices and techniques involved in the rehabilitation of the foot and section III explains the existing orthoses and exoskeletons for foot rehabilitation. Section IV discusses the construction and working of the prototype, and the results are presented in section V. Some concluding remarks and future scope is mentioned in section VI.

II. REHABILITATION TECHNIQUES

To understand the requirements and specifications of stroke rehabilitation devices, a brief introduction of existing techniques is given below [9].

A. Physiotherapy
The primary technique used is Physiotherapy which involves assessment of a Physiotherapist using various techniques. The techniques include various exercises.
1) Mobility training: To stabilise and strengthen to enhance balance and support.
2) Range of motion therapy: Helps in easing muscle tension allowing a good range of motion.
B. Technology-assisted
1) Functional electrical stimulation: This method involves inducing contraction to the weak muscles by application of electricity which helps in training them.
2) Game system technology: It is based on the idea of integration of games for rehabilitation. They involve functional activities and keep the patient occupied and motivated with games during the rehabilitation process.

III. EXISTING TECHNOLOGIES FOR REHABILITATION

Robotic exoskeletons have been employed in assisting individuals suffering from physical disability either for the advancement of therapy or as a permanent assistive tool. They are of various types, and can be classified based on their method of actuation:
- Rigid actuation: These devices are actuated using DC motors, Steppers etc.
- Soft actuation: These devices are actuated using compliant methods and are generally actuated pneumatically or using shape memory alloy (SMA) [10][13][14][15]. The AFO described in this paper falls under this category.
A. Rigid Actuation
1) Anklebot at Massachusetts Institute of Technology (MIT), USA: The Anklebot is a 3-DOF wearable robot, which is actuated by two linear screw actuators using two brushless dc motors. The linear actuators are mounted in parallel and provide actuation in two of the ankles 3-DOF, namely dorsiflexion-plantarflexion and inversioneversion [11]. Position information is provided by two sets of sensors: rotary encoders and linear encoders. No input is given by the user, and all movement is externally decided.
2) ALEX at University of Delaware, USA: This exoskeleton is mounted with a walker to support the device. The controller applies a force-field at the ankle of the subject. The linear actuators are mounted at the hip and knee of the orthosis. The torque generated by the actuators at these joints simulate the tangential forces needed to move the ankle of the subject along the trajectory [12]. The disadvantage is that it is not easily portable.
B. Soft Actuation
1) Wearable Soft Exoskeleton at Carnegie Mellon University, USA: The exoskeleton uses four PAMs placed on one of the lower legs (three anterior muscles for dorsiflexion, inversion, and eversion, and one posterior muscle for plantarflexion), which is connected to the knee brace and the foot brace with the help of artificial tendons. The artificial muscles were designed and placed as counterparts close to the biological muscles so that the device could provide additional forces to the corresponding muscles [13]. It is externally controlled using solenoid valves, and the sensors are used as position feedback for control without getting any input from the user. It helps with therapy, but it does not provide much independence for the user.
2) Powered ankle foot orthosis at University of Michigan, USA: This orthosis is actuated by PAMs providing only plantar flexion torque. It uses a real-time computer interface for controlling the air pressure supplied to the PAMs. The pressure is determined based on foot contact with the ground using a footswitch which is placed under the foot [14].
3) Adaptive control of actuated ankle foot orthosis (AAFO) at Paris-Est Crteil University, France: AAFO uses a predetermined trajectory of the ankles swing phase of the gait cycle, which helps in controlling the amount of assistance required for the ankle-foot orthosis. This method is employed as the current technologies are based on human/robot parameters, which are to be identified to set the magnitude of assistance required [15].

IV. CONSTRUCTION AND WORKING

A. Design of the Prototype

The design of the AFO focuses on achieving the following goals:
- User Comfort
- Minimal weight.
- Complete Range of Motion in a single axis.
- Simple setup.
- Minimal cost
1) Pneumatic Artificial Muscle Design: Each PAM consists of a silicone rubber tube, placed within a nylon mesh sleeve. The sleeve is kept in place with hose clamps on either end. One end is pneumatically sealed, and the other end is used as an inlet for pressurised air. Air is let in at around 40 psi. When air flows into the tube, it tends to expand volumetrically. The sleeves structure does not allow it to expand longitudinally, and rather, it expands radially while contracting longitudinally.

54 pt
0.75 in
19.1 mm

54 pt
0.75 in
19.1 mm

Multiple studies have been performed on these PAMs, and find the force-length characteristics to be similar to that of a muscle [16]. The materials used in the PAM are compliant, lightweight and low-cost. These properties make PAMs well suited for the AFO.

The required length and diameter of the PAMs were decided upon through experiments with various configurations, presented in Section V.


Fig. 2. AFOs Layout. Components labelled from (1) to (11): (1) Arduino Uno; (2) Motor drivers; (3) Solenoid Valves; (4) Li-Po; (5) Panel for electronic circuitry; (6) Knee braces; (7) PAM Mount; (8) PAM; (9) Foam padding; (10) Adjustable strings; (11) Orthotic Sole

2) Orthosis Design: The ground link of the Orthosis is located above the knee and functions and is connected to the second link around via a hinge joint. Another link is positioned on foot and acts as the end effector.

The brace and the sole are connected using two PAMs in an agonist-antagonist configuration, each one providing the necessary Dorsiflexion and Plantarflexion forces respectively. They can be modelled as slider mechanisms. The placement of the PAMs on the end is dependant on the required actuation torque and range of motion. Since PAMs are shown to provide a good amount of force [16], but only limited contraction, the choice was made to place them very close to the joint. This allows the AFO to achieve the entire Range of Motion which is roughly 20 degrees for dorsiflexion and 50 degrees for plantarflexion [17].

Some similar devices [18][19] have been constructed with the ground at the shin, connected to the ankle end effector in a similar fashion. We found that in this configuration, the transverse reaction forces during PAM contraction resulted in skin deformation at the skin-AFO interface. Such deformation was found to cause user discomfort and restrict the range of motion of the AFO. By placing the ground above the knee, the vector of reaction force is made almost completely normal to the skin-AFO interface as shown in Fig. 3.


Fig. 3. Interface between the skin and the orthosis


Fig. 4. Pneumatic Circuit

3) Electronics and Pneumatic Circuitry: Each PAM is controlled by a pair of 12V DC 2-Position 2-Way Solenoid Valves, where one acts as an inlet and the other acts as an outlet. Each pair of valves is connected to an L298N driver for logic. The drivers are connected to a Microcontroller Unit(MCU) (Arduino UNO). Two Myoware EMG sensors from Advancer Technologies are connected to the same MCU. The entire setup is powered by a 12V Lithium-Polymer Battery and placed on the ground link to optimise weight distribution throughout the AFO.
Both the inlet valves are connected to an air tank with pressurised air at 60psi, and the exhaust valves are left open to the atmosphere as shown in Fig.4. All pneumatic connections were made with 8 mm OD x 6 mm OD Polyurethane Pneumatic Tubes. The control methodologies for the PAMs are described in Section IV.B.4.
B. Control of the Orthosis
1) Signal Acquisition: In order to detect the intent of the user, the AFO uses EMG electrodes, connected to an MCU. Each McKibben muscle is placed so as to assist the functioning of a specific muscle. The targeted muscles are:
- Tibialis Anterior for Dorsiflexion
- Soleus for Plantarflexion
The positions of these muscles are depicted in Fig.5.
Each muscle requires a single non-invasive EMG sensor. Each sensor requires the placement of three electrodes to capture the differential component of the signal travelling across the muscle. As per EMG electrode placement standards [20], one electrode is placed near the centre of a muscle, one electrode near the end of a muscle and a ground electrode is placed near a bone for reference.

54 pt
0.75 in
19.1 mm

54 pt
0.75 in
19.1 mm


Fig. 5. Muscles of the leg Source: [21]

The rectified and integrated signal is passed from the signal pin of the sensor in the form of a 0 to 3.3V analog wave which is sampled by the 10-bit ADC of the MCU at a rate of 200Hz.


Fig. 6. Left: Electrode placement over the Tibialis Anterior Muscle; Right: Electrode placement over the Soleus Muscle

2) EMG Analysis: The rectified and integrated signals(signal envelopes) from the MyoWare muscle sensors were erratic and caused sudden spikes in the signal. To overcome this, the signals from both EMG sensors were passed to two independent 1-dimensional Kalman Filters, and the filtered output values of each iteration were taken as the estimated values for the next iteration. It was found that a Kalman Gain of 0.001 for both the filters gave the best results in removing noise from the signals, by inducing negligible latency in the filtered output as shown in Fig. 7. EMG signals for a muscle are highly dependant on a multitude of factors such as electrode placement, fatigue, and the physical and mental state of the user [22][23]. Hence, calibration is required before every session. This happens automatically on initialisation of the AFO. This calibration procedure sets the threshold for each muscle to enable intent estimation, which is described below.
The rest state characteristics of each muscle are obtained by recording the unfiltered EMG envelope for 10 seconds. The mean (µrest) and standard deviation (σrest) of this data


Fig. 7. EMG Signal Acquision, Filtering and Thresholding


Fig. 8. Intent Detection

are extracted from this data. Using the collected data, a threshold is calculated for each target muscle using (1) for Dorsiflexion and (2) for Plantarflexion. This threshold is then used to detect activation of each muscle. The muscle is found to be actively contracting when the filtered signal exceeds the threshold.
For Tibialis Anterior muscle, the threshold is determined by Eqn.1,
T = µrest +3σrest | (1)

For Soleus muscle, the threshold is determined by Eqn.2,

T = µrest +8σrest | (2)

Studies have shown that a threshold equal to the mean added to a multiple of the standard deviation gives good results when applied to the EMG envelope [24]. The values of the constant multiplier for standard deviation were determined experimentally, and the results of these tests are described in Section V.
3) Intent Detection Logic: Using the described method, it is possible to determine the state of a muscle in real time. Through experiments, it was found that the Soleus muscle was active during Plantarflexion and the initial, final stages of Dorsiflexion. This is visualized in Fig. 13, in which the patient performed Plantarflexion, followed by Dorsiflexion. Using this information, the User Intent can be detected by the method specified in Fig. 8

54 pt
0.75 in
19.1 mm

54 pt
0.75 in
19.1 mm
4) Control of PAM with EMG: The user closes the feedback loop by attempting to move their ankle by muscle contraction. This eliminates the need of external feedback, and allows real time intent detection.


Fig. 9. Operation Flowchart

In order to contract a PAM, pressurised air is inflated into it by opening the inlet valve and by closing the outlet valve. In order to relax (expand) a PAM, the air inside it is exhausted by closing the inlet valve and opening the outlet valve. The below table summarises the valve positions for different PAM configurations.

TABLE I

STATE OF SOLENOID VALVES

PAM movement | Inlet Valve | Exhaust Valve
Relax (Deflate) | Close | Open
Contract (Inflate) | Open | Close

In order to ensure smooth movement of the patients foot and avoid sudden movement, the speed of inflation/deflation of the PAMs was reduced by applying a Pulse Width Modulated(PWM) signal to the valves as shown in Fig. 10 and Fig.
11. Through experiments, it was found that a PWM signal with a time period of half a second and a duty cycle of 10% for 5 seconds was ideal.


Fig. 10. PWM Timing diagram during Inflation of the Muscle


Fig. 11. PWM Timing diagram during Exhaust of the Muscle

After detecting user intent, control signals from the MCU are sent to the pneumatic valves through the motor drivers. Table II describes the state of each PAM with respect to various user inputs.

TABLE II

STATE OF PNEUMATIC ARTIFICIAL MUSCLES

Intent | Dorsiflexor PAM | Plantarflexor PAM
Rest State | Relax | Relax
Plantarflexion | Relax | Contract
Dorsiflexion | Contract | Relax
V. RESULTS AND STATISTICAL DATA


Fig. 12. Prototype of the Ankle-Foot-Orthosis

A. Pneumatic Artificial Muscles Tests
The PAMs were tested by inflation at 35 psi with no external load to select the ideal contraction length required for the AFO.

TABLE III
PAM TESTS
Inner Diameter (inches) | Outer Diameter (inches) | Length of muscle (cm) | Length Contraction (cm) | Percentage Contraction (%)
1/3 | 1/2 | 20 | 2.5 | 12.5
1/2 | 5/8 | 20 | 1.8 | 9
1/3 | 1/2 | 30 | 5.1 | 17
1/2 | 5/8 | 30 | 3 | 10
B. EMG control Tests
The AFO was tested by three healthy individuals in two sessions each. The patients were asked to Flex their legs in a particular direction multiple times, and the percentage accuracy of intent detection was calculated.

TABLE IV

SESSION 1: SUBJECTS WERE WELL RESTED

Subject | Dorsiflexion Accuracy(%) | Plantarflexion accuracy(%)
1 | 95 | 95
2 | 100 | 90
3 | 95 | 90

54 pt
0.75 in
19.1 mm

54 pt
0.75 in
19.1 mm

TABLE V

SESSION 2: SUBJECTS WERE FATIGUED

Subject | Dorsiflexion Accuracy(%) | Plantarflexion accuracy(%)
1 | 95 | 90
2 | 90 | 90
3 | 90 | 90

From the above results, it is found that the simple control scheme presented is able to achieve a mean Dorsiflexion accuracy of 94.17%, and inaccuracies being 4.17% true-negative and 1.66% false-positive and. The mean Plantarflexion accuracy is 90.83% and the inaccuracies are 5.83% true-negative and 3.34% false-positive. It is worth noting that the accuracy decreases minimally when the patients are not wellrested. For well rested patients, the control scheme achieves a mean Dorsiflexor accuracy of 96.7% and inaccuracies being 1.65% false-positive and 1.65% true-negative. The mean Plantarflexion accuracy is 91.7% and the inaccuracies are 6.7% true-negative and 1.6% false-positive.


Fig. 13. Voltage-time graph obtained after the application of the Kalman Filter to both signals as well as the threshold lines

VI. CONCLUSIONS
The design and control of a 1 DOF Soft Ankle Foot Orthosis has been presented in this paper. The prototype shows promise to be as a therapeutic alternative. The AFO uses EMG signals which are reliable and easy to calibrate. The main purpose of the work is to replace the rigid and heavy hardware previously used for robotic rehabilitation. The AFO uses McKibben Muscles/PAMs, which are pneumatically actuated, low-cost and lightweight. The torque provided by the AFO can be increased by enhancing air pressure driving techniques, and this could allow the use of the device as a powered exoskeleton. Also, machine learning algorithms could be used to estimate the intent of the user with greater accuracy. The device could also be further developed by incorporating more degrees of freedom. This would allow the AFO to perform Inversion and Eversion of the leg.
| REFERENCES
[1] ”World Health Report” - 2002 from the World Health Organization Retrieved on: 10 May 2019 from http://www.who.int/whr/2002/en/.
[2] ”Walking abnormalities” MedlinePlus Retrieved on: 5 June 2019 from https://medlineplus.gov/ency/article/003199.htm
[3] Wiszomirska I, Bakiewicz M, Kaczmarczyk K, Brzuszkiewicz-Kumicka G, Wit A. Effect of Drop Foot on Spatiotemporal, Kinematic, and Kinetic Parameters during Gait. Appl Bionics Biomech. 2017;2017:3595461. doi:10.1155/2017/3595461.
[4] P. Langhorne, J. Bernhardt and G. Kwakkel, Stroke Rehabilitation, Stroke Care 2, The Lancet Vol 377, May 2011.
[5] K.X. Khor, H.A. Rahman, S.K. Fu et al. A Novel Hybrid Rehabilitation Robot for Upper and Lower Limbs Rehabilitation Training. Int. Conf. on Robot PRIDE (ConfPRIDE) 2013-2014, Procedia Computer Science 42 (2014) p. 293-300.
[6] A. Asokan and M. Vigneshwar, ”Design and Control of an EMG-based Low-cost Exoskeleton for Stroke Rehabilitation,” 2019 Fifth Indian Control Conference (ICC), New Delhi, India, 2019, pp. 478-483. doi: 10.1109/INDIANCC.2019.8715555
[7] Kim B, Deshpande AD. An Upper-Body Rehabilitation Exoskeleton Harmony with an Anatomical Shoulder Mechanism: Design, Modeling, Control, and Performance Evaluation. Int. Journal. of Robotics Research (IJRR) 2017, Vol 36 Issue 4, p. 414-435.
[8] J. C. Perry and J. Rosen.Design of a 7 Degree-of-Freedom Upper-Limb Powered Exoskeleton. The First IEEE/RAS-EMBS Int. Conf. on Biomedical Robotics and Biomechatronics, 2006. BioRob 2006., Pisa, 2006, pp. 805-810.
[9] | Stroke | rehabilitation: | What | to | expect | as | you | recover.
(May | 24, | 2017). | Retrieved | on | 2 | June | 2019, | from
https://www.mayoclinic.org/diseasesconditions/stroke/in-depth/strokerehabilitation/art-20045172
[10] K. Ikuta, ”Micro/miniature shape memory alloy actuator,” Proceedings., IEEE International Conference on Robotics and Automation, Cincinnati, OH, USA, 1990, pp. 2156-2161 vol.3. doi: 10.1109/ROBOT.1990.126323
[11] Roy, A., Krebs, H. I., Williams, D. J., Bever, C. T., Forrester, L. W., Macko, R. M., & Hogan, N. (2009). Robot-Aided Neurorehabilitation: A Novel Robot for Ankle Rehabilitation. IEEE Transactions on Robotics, 25(3), 569582. doi:10.1109/tro.2009.2019783
[12] Banala, S. K., Seok Hun Kim, Agrawal, S. K., & Scholz, J. P. (2009). Robot Assisted Gait Training With Active Leg Exoskeleton (ALEX). IEEE Transactions on Neural Systems and Rehabilitation Engineering, 17(1), 28.doi:10.1109/tnsre.2008.2008280
[13] Park, Y.-L., Chen, B., Prez-Arancibia, N. O., Young, D., Stirling, L., Wood, R. J., Nagpal, R. (2014). Design and control of a bio-inspired soft wearable robotic device for anklefoot rehabilitation. Bioinspiration & Biomimetics, 9(1), 016007.doi:10.1088/1748-3182/9/1/016007
[14] Gordon, K. E., Sawicki, G. S., & Ferris, D. P. (2006). Mechanical performance of artificial pneumatic muscles to power an anklefoot orthosis. Journal of Biomechanics, 39(10), 18321841.doi:10.1016/j.jbiomech.2005.05.018
[15] Arnez-Paniagua, V., Rifai, H., Amirat, Y., & Mohammed, S. (2017). Adaptive control of an actuated-ankle-foot-orthosis. 2017 International Conference on Rehabilitation Robotics (ICORR). doi:10.1109/icorr.2017.8009474
[16] Takosoglu, Jakub & Laski, P & Blasiak, Slawomir & Bracha, Gabriel & Pietrala, Dawid. (2016). Determining the Static Characteristics of Pneumatic Muscles. Measurement and Control. 49. 62-71. 10.1177/0020294016629176.
[17] ”Generally Accepted Values for Normal Range of Motion (ROM) in Joints” (May 14, 2019) Retrieved on 8 June 2019 from https://www.verywellhealth.com/what-is-normal-range-of-motion-ina-joint-3120361
[18] Ferris DP, Czerniecki JM, Hannaford B. An ankle-foot orthosis powered by artificial pneumatic muscles. J Appl Biomech. 2005;21(2):189197.
[19] Zhu, Y. (2017). Design and web-based control of a soft ankle foot orthosis. 17. 82-88.
[20] Datasheet Retrieved on 8 June 2019 from https://cdn.sparkfun.com/datasheets/Sensors/Biometric/MyowareUserManualAT-04-001.pdf
[21] ”Appendicular | Muscles | of | the | Pelvic | Girdle | and
Lower | Limbs” | Retrieved | on | 8 | July | 2019 | from
https://cnx.org/contents/FPtK1zmh@8.108:y9 gDy74@5/Appendicular-Muscles-of-the-Pelvic-Girdle-and-Lower-Limbs
[22] Jamal, Muhammad. (2012). Signal Acquisition Using Surface EMG and Circuit Design Considerations for Robotic Prosthesis. Computational Intelligence in Electromyography Analysis - A Perspective on Current Applications and Future Challenges. 10.5772/52556.
[23] M. B. I. Reaz, M. S. Hussain, F. Mohd-Yasin. Techniques of EMG signal analysis: detection, processing, classification and applications. Biol. Proced. Online 2006; 8(1): 11-35.
[24] K. T. O zgunen, U. C elik, S. S. Kurdak. Determination of an optimal threshold value for muscle activity detection in EMG analysis. Journal of Sports Science and Medicine (2010) 9, pp. 620-628.

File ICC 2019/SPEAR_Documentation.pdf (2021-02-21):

## Design and Control of a Low-cost EMG-based Soft Robotic Ankle-Foot Orthosis for Foot Drop Rehabilitation*

Nitish Gudapati¹

, Koushik Kumaran²

, Deepak S V³

, Mukesh Kanna R⁴

, Jinesh R⁵
, Himadri Poddar⁶

Abstract— Stroke patients often suffer from foot drop, a gait abnormality usually due to the paralysis of the anterior portion muscles of the lower leg, causing an inability or impaired ability to raise the foot at the ankle joint. This leads to extremities of the foot being dragged along the ground while walking, causing tripping and other accidents. Braces or splints that fit into shoes are prescribed to help hold the foot in a normal position. For rehabilitation, most patients are trained to walk with canes, and therapists prescribe physiotherapy for a series of short, intensive sessions. These solutions are expensive and slow processes as they require the presence of skilled personnel and are carried out for short durations. In this paper, we present a novel design and control methodology for a 1-DoF Soft Active Ankle-Foot Orthosis (AFO) to address these issues. The AFO is designed to augment the human musculoskeletal system. The AFO is actuated using McKibben Muscles (Pneumatic Artificial Muscles), which are driven pneumatically. They are cost-effective and lightweight, offering a significant advantage over Motor Driven orthoses. The orthosis is controlled using Electromyography(EMG) signals from the muscles involved in the motion of the ankle. The use of EMG signals for control is found to be a better option than existing methods due to its non-invasive nature. It is also found to be simple and cost-effective for intent detection.

Keywords: Active-Foot-Orthosis, Electromyography (EMG), Foot Drop, Rehabilitation, Soft Robotics

I. INTRODUCTION
According to the World Health Organization, 15 million people suffer stroke worldwide each year. Of these, 5 million people die, and another 5 million are permanently disabled [1]. A common ailment for stroke survivors is foot drop, i.e., the inability to actively perform Dorsiflexion the foot. This leads to the occurrence of steppage gait, where the foot drags

*This work was supported by Institute grants through the Robotics and Machine Intelligence Club, NIT Tiruchirappalli, INDIA.
1Nitish Gudapati is a student at the Department of Mechanical Engineering, National Institute of Technology - Tiruchirappalli, Tiruchirappalli, Tamil Nadu 620015, INDIA gudapatinitish9@gmail.com 2Koushik Kumaran is a student at the Department of Electronics and Communication Engineering, National Institute of Technology - Tiruchirappalli, Tiruchirappalli, Tamil Nadu 620015, INDIA koushikkumaran52@gmail.com
3Deepak S V is a student at the Department of Electrical and Electronics Engineering, National Institute of Technology - Tiruchirappalli, Tiruchirappalli, Tamil Nadu 620015, INDIA svdeepak99@gmail.com 4Mukesh Kanna R is a student at the Department of Mechanical Engineering, National Institute of Technology - Tiruchirappalli, Tiruchirappalli, Tamil Nadu 620015, INDIA kanna.r1999@gmail.com
5
Jinesh R S is a student at the Department of Electrical and Electronics Engineering, National Institute of Technology - Tiruchirappalli, Tiruchirappalli, Tamil Nadu 620015, INDIA jineshrs2398@gmail.com 6Himadri Poddar is a student at the Department of Instrumentation and Control Engineering, National Institute of Technology - Tiruchirappalli, Tiruchirappalli, Tamil Nadu 620015, INDIA himadripoddar.nitt@gmail.com

along, requiring the patient to raise their knee higher than usual in the swing phase to counter this [2]. The patient’s foot slaps the ground during the foot strike phase of the gait cycle. Studies have shown that the entire kinematic chain of the lower body is disturbed, resulting in the functioning of the motor system under abnormal load [3].
Patients generally undergo therapy to regain motor control, and the required recovery can take from months to years to complete as shown in Fig.1 [4]. The available number of medical professionals are far less than the requirement, and they may not be accessible to all those who need it [5]. To this end, robotic devices can significantly decrease the burden on therapists and caregivers and can be used to provide intensive task-oriented practice.


Fig. 1. A hypothetical pattern of recovery after stroke with the timing of intervention strategies Source: [4]

Considerable research has gone into developing such robotic devices, especially for upper-body rehabilitation [6]
[7] [8]. Most of these devices, however, are rigid, heavy and unwieldy. In recent years, the interest in a compliant robotic system has increased exponentially, due to the significant advantages they provide. Mckibben muscles or Pneumatic Artificial Muscles (PAM) are a possible actuation method with properties that make them uniquely suited for the application presented. These properties are explored in depth in Section IV.
In this paper, we describe the design and control of a single DOF orthosis, actuated with PAMs and controlled with Electromyography(EMG) Signals. The EMG sensors are non-invasive, and all computation and control required for the operation of the orthosis runs onboard the orthosis in real time. The design is compliant, lightweight and wearable. Section II explains the practices and techniques involved in the rehabilitation of the foot and section III explains the existing orthoses and exoskeletons for foot rehabilitation. Section IV discusses the construction and working of the prototype, and the results are presented in section V. Some concluding remarks and future scope is mentioned in section VI.

II. REHABILITATION TECHNIQUES

To understand the requirements and specifications of stroke rehabilitation devices, a brief introduction of existing techniques is given below [9].

A. Physiotherapy
The primary technique used is Physiotherapy which involves assessment of a Physiotherapist using various techniques. The techniques include various exercises.
1) Mobility training: To stabilise and strengthen to enhance balance and support.
2) Range of motion therapy: Helps in easing muscle tension allowing a good range of motion.
B. Technology-assisted
1) Functional electrical stimulation: This method involves inducing contraction to the weak muscles by application of electricity which helps in training them.
2) Game system technology: It is based on the idea of integration of games for rehabilitation. They involve functional activities and keep the patient occupied and motivated with games during the rehabilitation process.

III. EXISTING TECHNOLOGIES FOR REHABILITATION

Robotic exoskeletons have been employed in assisting individuals suffering from physical disability either for the advancement of therapy or as a permanent assistive tool. They are of various types, and can be classified based on their method of actuation:
- Rigid actuation: These devices are actuated using DC motors, Steppers etc.
- Soft actuation: These devices are actuated using compliant methods and are generally actuated pneumatically or using shape memory alloy (SMA) [10][13][14][15]. The AFO described in this paper falls under this category.
A. Rigid Actuation
1) Anklebot at Massachusetts Institute of Technology (MIT), USA: The Anklebot is a 3-DOF wearable robot, which is actuated by two linear screw actuators using two brushless dc motors. The linear actuators are mounted in parallel and provide actuation in two of the ankles 3-DOF, namely dorsiflexion-plantarflexion and inversioneversion [11]. Position information is provided by two sets of sensors: rotary encoders and linear encoders. No input is given by the user, and all movement is externally decided.
2) ALEX at University of Delaware, USA: This exoskeleton is mounted with a walker to support the device. The controller applies a force-field at the ankle of the subject. The linear actuators are mounted at the hip and knee of the orthosis. The torque generated by the actuators at these joints simulate the tangential forces needed to move the ankle of the subject along the trajectory [12]. The disadvantage is that it is not easily portable.
B. Soft Actuation
1) Wearable Soft Exoskeleton at Carnegie Mellon University, USA: The exoskeleton uses four PAMs placed on one of the lower legs (three anterior muscles for dorsiflexion, inversion, and eversion, and one posterior muscle for plantarflexion), which is connected to the knee brace and the foot brace with the help of artificial tendons. The artificial muscles were designed and placed as counterparts close to the biological muscles so that the device could provide additional forces to the corresponding muscles [13]. It is externally controlled using solenoid valves, and the sensors are used as position feedback for control without getting any input from the user. It helps with therapy, but it does not provide much independence for the user.
2) Powered ankle foot orthosis at University of Michigan, USA: This orthosis is actuated by PAMs providing only plantar flexion torque. It uses a real-time computer interface for controlling the air pressure supplied to the PAMs. The pressure is determined based on foot contact with the ground using a footswitch which is placed under the foot [14].
3) Adaptive control of actuated ankle foot orthosis (AAFO) at Paris-Est Crteil University, France: AAFO uses a predetermined trajectory of the ankles swing phase of the gait cycle, which helps in controlling the amount of assistance required for the ankle-foot orthosis. This method is employed as the current technologies are based on human/robot parameters, which are to be identified to set the magnitude of assistance required [15].

IV. CONSTRUCTION AND WORKING

A. Design of the Prototype

The design of the AFO focuses on achieving the following goals:
- User Comfort
- Minimal weight.
- Complete Range of Motion in a single axis.
- Simple setup.
- Minimal cost
1) Pneumatic Artificial Muscle Design: Each PAM consists of a silicone rubber tube, placed within a nylon mesh sleeve. The sleeve is kept in place with hose clamps on either end. One end is pneumatically sealed, and the other end is used as an inlet for pressurised air. Air is let in at around 40 psi. When air flows into the tube, it tends to expand volumetrically. The sleeves structure does not allow it to expand longitudinally, and rather, it expands radially while contracting longitudinally.

Multiple studies have been performed on these PAMs, and find the force-length characteristics to be similar to that of a muscle [16]. The materials used in the PAM are compliant, lightweight and low-cost. These properties make PAMs well suited for the AFO.

The required length and diameter of the PAMs were decided upon through experiments with various configurations, presented in Section V.


Fig. 2. AFOs Layout. Components labelled from (1) to (11): (1) Arduino Uno; (2) Motor drivers; (3) Solenoid Valves; (4) Li-Po; (5) Panel for electronic circuitry; (6) Knee braces; (7) PAM Mount; (8) PAM; (9) Foam padding; (10) Adjustable strings; (11) Orthotic Sole

2) Orthosis Design: The ground link of the Orthosis is located above the knee and functions and is connected to the second link around via a hinge joint. Another link is positioned on foot and acts as the end effector.

The brace and the sole are connected using two PAMs in an agonist-antagonist configuration, each one providing the necessary Dorsiflexion and Plantarflexion forces respectively. They can be modelled as slider mechanisms. The placement of the PAMs on the end is dependant on the required actuation torque and range of motion. Since PAMs are shown to provide a good amount of force [16], but only limited contraction, the choice was made to place them very close to the joint. This allows the AFO to achieve the entire Range of Motion which is roughly 20 degrees for dorsiflexion and 50 degrees for plantarflexion [17].

Some similar devices [18][19] have been constructed with the ground at the shin, connected to the ankle end effector in a similar fashion. We found that in this configuration, the transverse reaction forces during PAM contraction resulted in skin deformation at the skin-AFO interface. Such deformation was found to cause user discomfort and restrict the range of motion of the AFO. By placing the ground above the knee, the vector of reaction force is made almost completely normal to the skin-AFO interface as shown in Fig. 3.


Fig. 3. Interface between the skin and the orthosis


Fig. 4. Pneumatic Circuit

3) Electronics and Pneumatic Circuitry: Each PAM is controlled by a pair of 12V DC 2-Position 2-Way Solenoid Valves, where one acts as an inlet and the other acts as an outlet. Each pair of valves is connected to an L298N driver for logic. The drivers are connected to a Microcontroller Unit(MCU) (Arduino UNO). Two Myoware EMG sensors from Advancer Technologies are connected to the same MCU. The entire setup is powered by a 12V Lithium-Polymer Battery and placed on the ground link to optimise weight distribution throughout the AFO.
Both the inlet valves are connected to an air tank with pressurised air at 60psi, and the exhaust valves are left open to the atmosphere as shown in Fig.4. All pneumatic connections were made with 8 mm OD x 6 mm OD Polyurethane Pneumatic Tubes. The control methodologies for the PAMs are described in Section IV.B.4.
B. Control of the Orthosis
1) Signal Acquisition: In order to detect the intent of the user, the AFO uses EMG electrodes, connected to an MCU. Each McKibben muscle is placed so as to assist the functioning of a specific muscle. The targeted muscles are:
- Tibialis Anterior for Dorsiflexion
- Soleus for Plantarflexion
The positions of these muscles are depicted in Fig.5.
Each muscle requires a single non-invasive EMG sensor. Each sensor requires the placement of three electrodes to capture the differential component of the signal travelling across the muscle. As per EMG electrode placement standards [20], one electrode is placed near the centre of a muscle, one electrode near the end of a muscle and a ground electrode is placed near a bone for reference.


Fig. 5. Muscles of the leg Source: [21]

The rectified and integrated signal is passed from the signal pin of the sensor in the form of a 0 to 3.3V analog wave which is sampled by the 10-bit ADC of the MCU at a rate of 200Hz.


Fig. 6. Left: Electrode placement over the Tibialis Anterior Muscle; Right: Electrode placement over the Soleus Muscle

2) EMG Analysis: The rectified and integrated signals(signal envelopes) from the MyoWare muscle sensors were erratic and caused sudden spikes in the signal. To overcome this, the signals from both EMG sensors were passed to two independent 1-dimensional Kalman Filters, and the filtered output values of each iteration were taken as the estimated values for the next iteration. It was found that a Kalman Gain of 0.001 for both the filters gave the best results in removing noise from the signals, by inducing negligible latency in the filtered output as shown in Fig. 7. EMG signals for a muscle are highly dependant on a multitude of factors such as electrode placement, fatigue, and the physical and mental state of the user [22][23]. Hence, calibration is required before every session. This happens automatically on initialisation of the AFO. This calibration procedure sets the threshold for each muscle to enable intent estimation, which is described below.
The rest state characteristics of each muscle are obtained by recording the unfiltered EMG envelope for 10 seconds. The mean (µrest) and standard deviation (σrest) of this data


Fig. 7. EMG Signal Acquision, Filtering and Thresholding


Fig. 8. Intent Detection

are extracted from this data. Using the collected data, a threshold is calculated for each target muscle using (1) for Dorsiflexion and (2) for Plantarflexion. This threshold is then used to detect activation of each muscle. The muscle is found to be actively contracting when the filtered signal exceeds the threshold.
For Tibialis Anterior muscle, the threshold is determined by Eqn.1,
T = µrest +3σrest | (1)

For Soleus muscle, the threshold is determined by Eqn.2,

T = µrest +8σrest | (2)

Studies have shown that a threshold equal to the mean added to a multiple of the standard deviation gives good results when applied to the EMG envelope [24]. The values of the constant multiplier for standard deviation were determined experimentally, and the results of these tests are described in Section V.
3) Intent Detection Logic: Using the described method, it is possible to determine the state of a muscle in real time. Through experiments, it was found that the Soleus muscle was active during Plantarflexion and the initial, final stages of Dorsiflexion. This is visualized in Fig. 13, in which the patient performed Plantarflexion, followed by Dorsiflexion. Using this information, the User Intent can be detected by the method specified in Fig. 8

4) Control of PAM with EMG: The user closes the feedback loop by attempting to move their ankle by muscle contraction. This eliminates the need of external feedback, and allows real time intent detection.


Fig. 9. Operation Flowchart

In order to contract a PAM, pressurised air is inflated into it by opening the inlet valve and by closing the outlet valve. In order to relax (expand) a PAM, the air inside it is exhausted by closing the inlet valve and opening the outlet valve. The below table summarises the valve positions for different PAM configurations.

TABLE I

STATE OF SOLENOID VALVES

PAM movement | Inlet Valve | Exhaust Valve
Relax (Deflate) | Close | Open
Contract (Inflate) | Open | Close

In order to ensure smooth movement of the patients foot and avoid sudden movement, the speed of inflation/deflation of the PAMs was reduced by applying a Pulse Width Modulated(PWM) signal to the valves as shown in Fig. 10 and Fig.
11. Through experiments, it was found that a PWM signal with a time period of half a second and a duty cycle of 10% for 5 seconds was ideal.


Fig. 10. PWM Timing diagram during Inflation of the Muscle


Fig. 11. PWM Timing diagram during Exhaust of the Muscle

After detecting user intent, control signals from the MCU are sent to the pneumatic valves through the motor drivers. Table II describes the state of each PAM with respect to various user inputs.

TABLE II

STATE OF PNEUMATIC ARTIFICIAL MUSCLES

Intent | Dorsiflexor PAM | Plantarflexor PAM
Rest State | Relax | Relax
Plantarflexion | Relax | Contract
Dorsiflexion | Contract | Relax
V. RESULTS AND STATISTICAL DATA


Fig. 12. Prototype of the Ankle-Foot-Orthosis

A. Pneumatic Artificial Muscles Tests
The PAMs were tested by inflation at 35 psi with no external load to select the ideal contraction length required for the AFO.

TABLE III
PAM TESTS
Inner Diameter (inches) | Outer Diameter (inches) | Length of muscle (cm) | Length Contraction (cm) | Percentage Contraction (%)
1/3 | 1/2 | 20 | 2.5 | 12.5
1/2 | 5/8 | 20 | 1.8 | 9
1/3 | 1/2 | 30 | 5.1 | 17
1/2 | 5/8 | 30 | 3 | 10
B. EMG control Tests
The AFO was tested by three healthy individuals in two sessions each. The patients were asked to Flex their legs in a particular direction multiple times, and the percentage accuracy of intent detection was calculated.

TABLE IV

SESSION 1: SUBJECTS WERE WELL RESTED

Subject | Dorsiflexion Accuracy(%) | Plantarflexion accuracy(%)
1 | 95 | 95
2 | 100 | 90
3 | 95 | 90

TABLE V

SESSION 2: SUBJECTS WERE FATIGUED

Subject | Dorsiflexion Accuracy(%) | Plantarflexion accuracy(%)
1 | 95 | 90
2 | 90 | 90
3 | 90 | 90

From the above results, it is found that the simple control scheme presented is able to achieve a mean Dorsiflexion accuracy of 94.17%, and inaccuracies being 4.17% true-negative and 1.66% false-positive and. The mean Plantarflexion accuracy is 90.83% and the inaccuracies are 5.83% true-negative and 3.34% false-positive. It is worth noting that the accuracy decreases minimally when the patients are not wellrested. For well rested patients, the control scheme achieves a mean Dorsiflexor accuracy of 96.7% and inaccuracies being 1.65% false-positive and 1.65% true-negative. The mean Plantarflexion accuracy is 91.7% and the inaccuracies are 6.7% true-negative and 1.6% false-positive.


Fig. 13. Voltage-time graph obtained after the application of the Kalman Filter to both signals as well as the threshold lines

VI. CONCLUSIONS
The design and control of a 1 DOF Soft Ankle Foot Orthosis has been presented in this paper. The prototype shows promise to be as a therapeutic alternative. The AFO uses EMG signals which are reliable and easy to calibrate. The main purpose of the work is to replace the rigid and heavy hardware previously used for robotic rehabilitation. The AFO uses McKibben Muscles/PAMs, which are pneumatically actuated, low-cost and lightweight. The torque provided by the AFO can be increased by enhancing air pressure driving techniques, and this could allow the use of the device as a powered exoskeleton. Also, machine learning algorithms could be used to estimate the intent of the user with greater accuracy. The device could also be further developed by incorporating more degrees of freedom. This would allow the AFO to perform Inversion and Eversion of the leg.
| REFERENCES
[1] ”World Health Report” - 2002 from the World Health Organization Retrieved on: 10 May 2019 from http://www.who.int/whr/2002/en/.
[2] ”Walking abnormalities” MedlinePlus Retrieved on: 5 June 2019 from https://medlineplus.gov/ency/article/003199.htm
[3] Wiszomirska I, Bakiewicz M, Kaczmarczyk K, Brzuszkiewicz-Kumicka G, Wit A. Effect of Drop Foot on Spatiotemporal, Kinematic, and Kinetic Parameters during Gait. Appl Bionics Biomech. 2017;2017:3595461. doi:10.1155/2017/3595461.
[4] P. Langhorne, J. Bernhardt and G. Kwakkel, Stroke Rehabilitation, Stroke Care 2, The Lancet Vol 377, May 2011.
[5] K.X. Khor, H.A. Rahman, S.K. Fu et al. A Novel Hybrid Rehabilitation Robot for Upper and Lower Limbs Rehabilitation Training. Int. Conf. on Robot PRIDE (ConfPRIDE) 2013-2014, Procedia Computer Science 42 (2014) p. 293-300.
[6] A. Asokan and M. Vigneshwar, ”Design and Control of an EMG-based Low-cost Exoskeleton for Stroke Rehabilitation,” 2019 Fifth Indian Control Conference (ICC), New Delhi, India, 2019, pp. 478-483. doi: 10.1109/INDIANCC.2019.8715555
[7] Kim B, Deshpande AD. An Upper-Body Rehabilitation Exoskeleton Harmony with an Anatomical Shoulder Mechanism: Design, Modeling, Control, and Performance Evaluation. Int. Journal. of Robotics Research (IJRR) 2017, Vol 36 Issue 4, p. 414-435.
[8] J. C. Perry and J. Rosen.Design of a 7 Degree-of-Freedom Upper-Limb Powered Exoskeleton. The First IEEE/RAS-EMBS Int. Conf. on Biomedical Robotics and Biomechatronics, 2006. BioRob 2006., Pisa, 2006, pp. 805-810.
[9] | Stroke | rehabilitation: | What | to | expect | as | you | recover.
(May | 24, | 2017). | Retrieved | on | 2 | June | 2019, | from
https://www.mayoclinic.org/diseasesconditions/stroke/in-depth/strokerehabilitation/art-20045172
[10] K. Ikuta, ”Micro/miniature shape memory alloy actuator,” Proceedings., IEEE International Conference on Robotics and Automation, Cincinnati, OH, USA, 1990, pp. 2156-2161 vol.3. doi: 10.1109/ROBOT.1990.126323
[11] Roy, A., Krebs, H. I., Williams, D. J., Bever, C. T., Forrester, L. W., Macko, R. M., & Hogan, N. (2009). Robot-Aided Neurorehabilitation: A Novel Robot for Ankle Rehabilitation. IEEE Transactions on Robotics, 25(3), 569582. doi:10.1109/tro.2009.2019783
[12] Banala, S. K., Seok Hun Kim, Agrawal, S. K., & Scholz, J. P. (2009). Robot Assisted Gait Training With Active Leg Exoskeleton (ALEX). IEEE Transactions on Neural Systems and Rehabilitation Engineering, 17(1), 28.doi:10.1109/tnsre.2008.2008280
[13] Park, Y.-L., Chen, B., Prez-Arancibia, N. O., Young, D., Stirling, L., Wood, R. J., Nagpal, R. (2014). Design and control of a bio-inspired soft wearable robotic device for anklefoot rehabilitation. Bioinspiration & Biomimetics, 9(1), 016007.doi:10.1088/1748-3182/9/1/016007
[14] Gordon, K. E., Sawicki, G. S., & Ferris, D. P. (2006). Mechanical performance of artificial pneumatic muscles to power an anklefoot orthosis. Journal of Biomechanics, 39(10), 18321841.doi:10.1016/j.jbiomech.2005.05.018
[15] Arnez-Paniagua, V., Rifai, H., Amirat, Y., & Mohammed, S. (2017). Adaptive control of an actuated-ankle-foot-orthosis. 2017 International Conference on Rehabilitation Robotics (ICORR). doi:10.1109/icorr.2017.8009474
[16] Takosoglu, Jakub & Laski, P & Blasiak, Slawomir & Bracha, Gabriel & Pietrala, Dawid. (2016). Determining the Static Characteristics of Pneumatic Muscles. Measurement and Control. 49. 62-71. 10.1177/0020294016629176.
[17] ”Generally Accepted Values for Normal Range of Motion (ROM) in Joints” (May 14, 2019) Retrieved on 8 June 2019 from https://www.verywellhealth.com/what-is-normal-range-of-motion-ina-joint-3120361
[18] Ferris DP, Czerniecki JM, Hannaford B. An ankle-foot orthosis powered by artificial pneumatic muscles. J Appl Biomech. 2005;21(2):189197.
[19] Zhu, Y. (2017). Design and web-based control of a soft ankle foot orthosis. 17. 82-88.
[20] Datasheet Retrieved on 8 June 2019 from https://cdn.sparkfun.com/datasheets/Sensors/Biometric/MyowareUserManualAT-04-001.pdf
[21] ”Appendicular | Muscles | of | the | Pelvic | Girdle | and
Lower | Limbs” | Retrieved | on | 8 | July | 2019 | from
https://cnx.org/contents/FPtK1zmh@8.108:y9 gDy74@5/Appendicular-Muscles-of-the-Pelvic-Girdle-and-Lower-Limbs
[22] Jamal, Muhammad. (2012). Signal Acquisition Using Surface EMG and Circuit Design Considerations for Robotic Prosthesis. Computational Intelligence in Electromyography Analysis - A Perspective on Current Applications and Future Challenges. 10.5772/52556.
[23] M. B. I. Reaz, M. S. Hussain, F. Mohd-Yasin. Techniques of EMG signal analysis: detection, processing, classification and applications. Biol. Proced. Online 2006; 8(1): 11-35.
[24] K. T. O zgunen, U. C elik, S. S. Kurdak. Determination of an optimal threshold value for muscle activity detection in EMG analysis. Journal of Sports Science and Medicine (2010) 9, pp. 620-628.

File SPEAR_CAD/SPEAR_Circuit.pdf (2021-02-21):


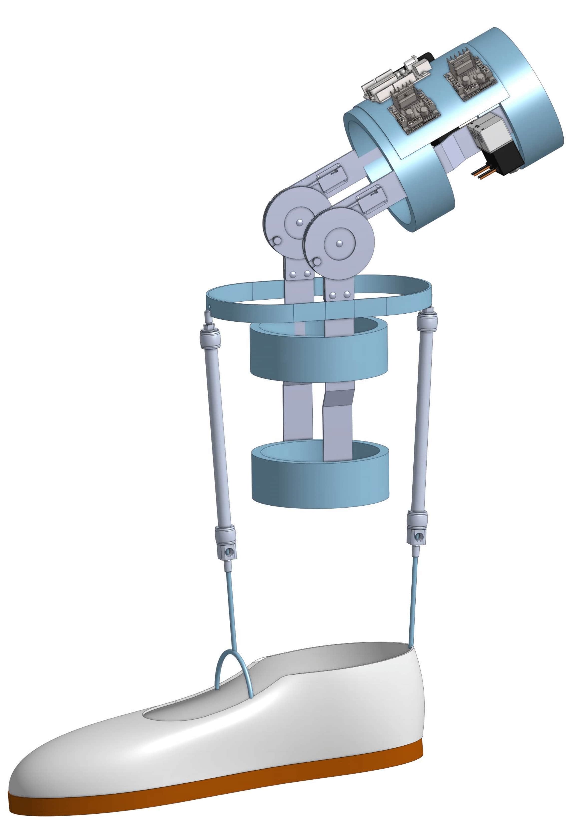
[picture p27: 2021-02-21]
SPEAR_CAD/SPEAR_Left-1.jpg

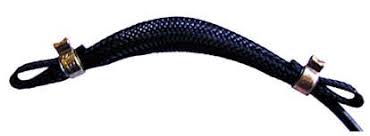
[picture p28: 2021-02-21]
ICC 2019/Latex Pics/airmuscle.jpg

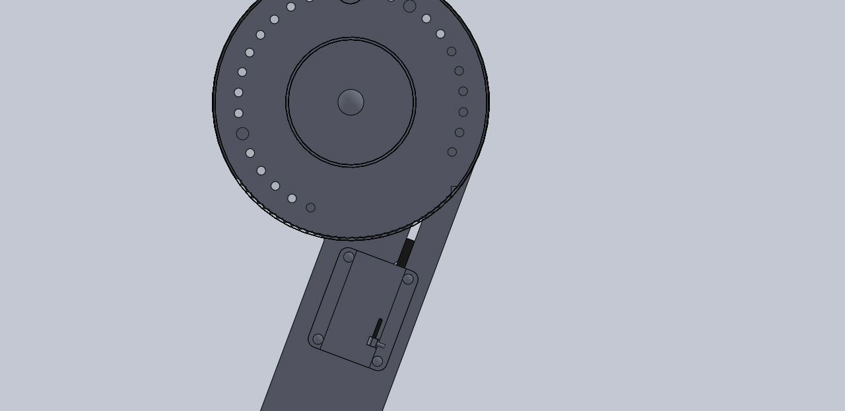
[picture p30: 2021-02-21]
SPEAR_CAD/Part_Files/a-ratchet-hinge-for-knee-elbow-orthotics-1.snapshot.6/Renderings/bracehinge free.JPG

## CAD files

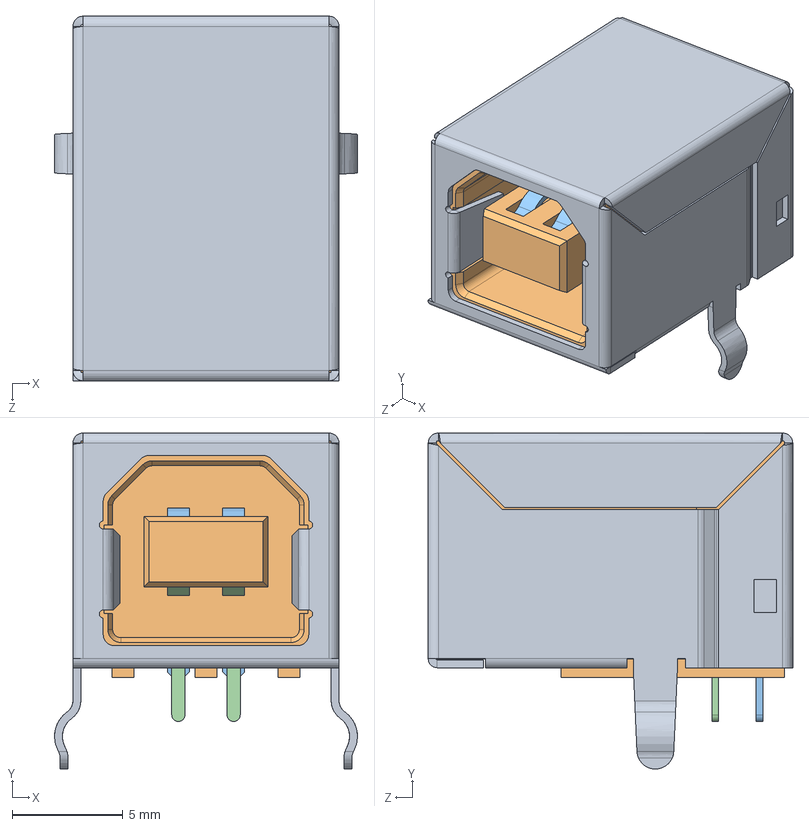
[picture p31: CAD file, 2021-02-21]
SPEAR_CAD/Part_Files/arduino-uno-r3-1.snapshot.3/arduino II/USB type b.SLDPRT.SLDASM
13.7 x 15.2 x 16.5 mm
USB SHELL
USB core
usb top contact x 2
usb btm contact x 2

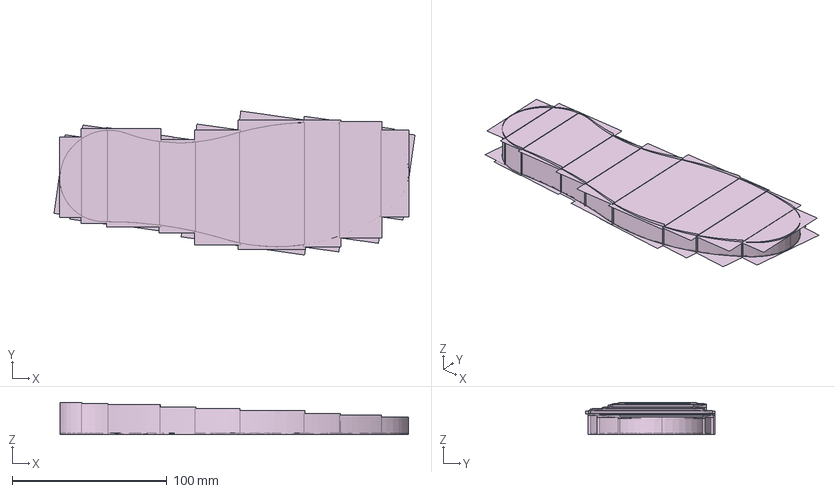
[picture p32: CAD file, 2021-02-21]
SPEAR_CAD/Part_Files/shoes-sole-1.snapshot.1/shoes sole/updatedshoesole_asm.igs
233.3 x 93.1 x 20.8 mm

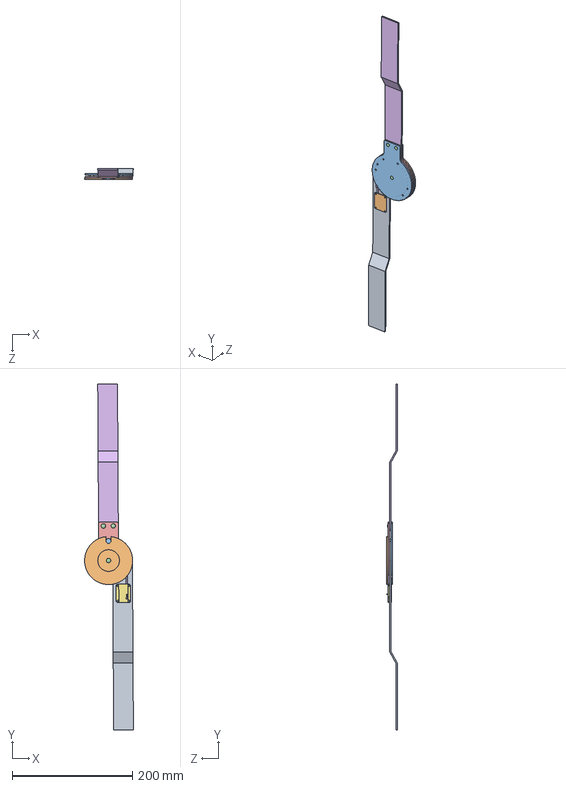
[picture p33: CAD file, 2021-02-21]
SPEAR_CAD/Part_Files/a-ratchet-hinge-for-knee-elbow-orthotics-1.snapshot.6/brace hinge/bracehinge.SLDASM
81.2 x 575.8 x 17.9 mm
middlepivot
pawlcover
bottomratchet
largescrew2 x 2
topratchet
upperstrut
pawltopcover
smallscrew x 4
smallscrew2 x 2
cover
largescrew
mainscrew
slide
pawl

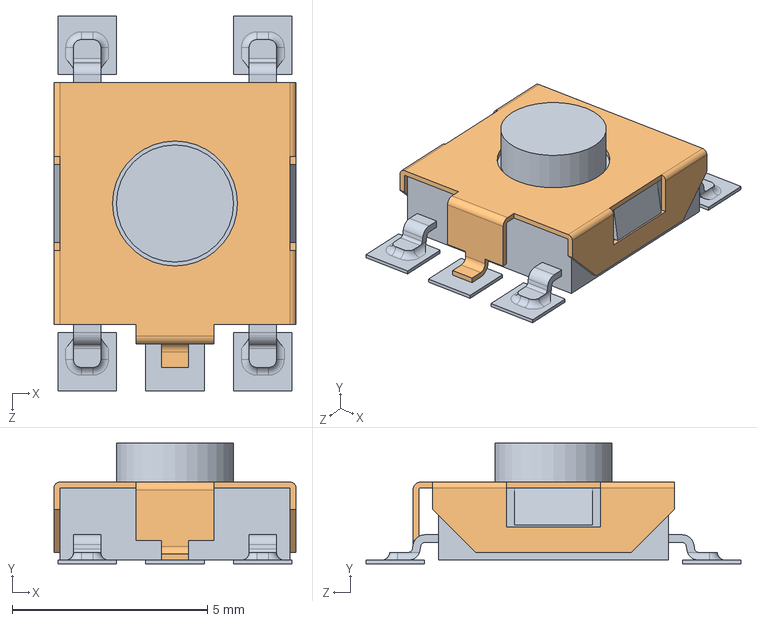
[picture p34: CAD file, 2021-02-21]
SPEAR_CAD/Part_Files/arduino-uno-r3-1.snapshot.3/arduino II/RESET BUTTON.SLDASM
6.20 x 3.10 x 9.60 mm
RESET CORE
RESET

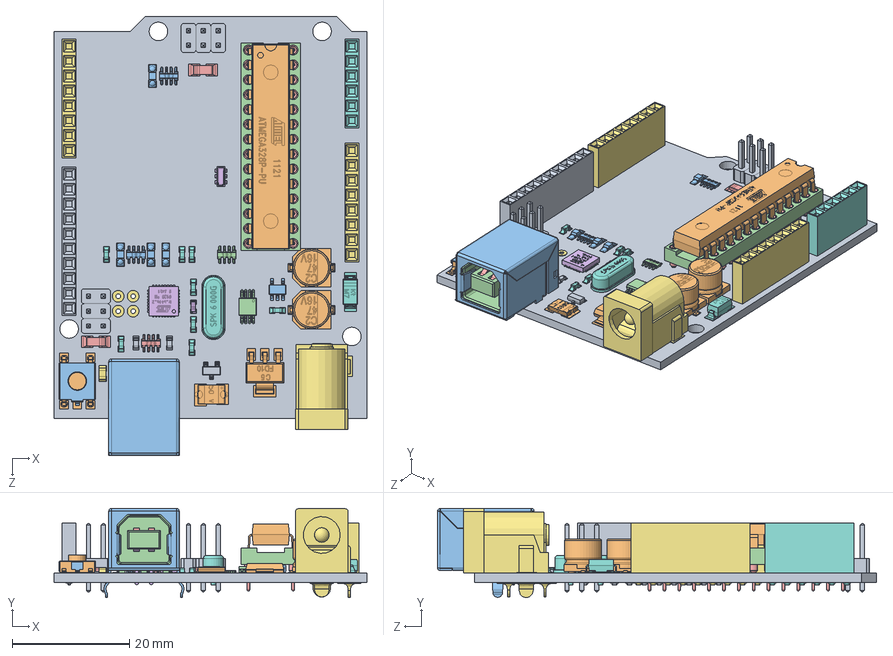
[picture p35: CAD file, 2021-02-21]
SPEAR_CAD/Part_Files/arduino-uno-r3-1.snapshot.3/arduino uno/arduino uno.SLDASM
53.3 x 15.2 x 74.9 mm
unoboard blue
47uf CAP Dcase x 2
USB SHELL
USB core
usb top contact x 2
usb btm contact x 2
power jack
crystal
2pin_header__02 x 6
nano - reg
led x 4
dip28
dip socket pin x 28
atmega16u2
8 PORT HEADER x 2
6 PORT HEADER
10 PORT HEADER
ATMEL328P
102 RESISTOR PACK x 2
103 RESISTOR PACK
220 RESISTOR PACK
16mhz crystal - measured
PADS001
603 cap on pad x 8
ssot3
mf-msmf050-2
lmv358
lp2985dgkr
cd1206 diode x 2
603 resistor
blm21
m7 diode
MLC0603 x 2
RESET CORE
RESET

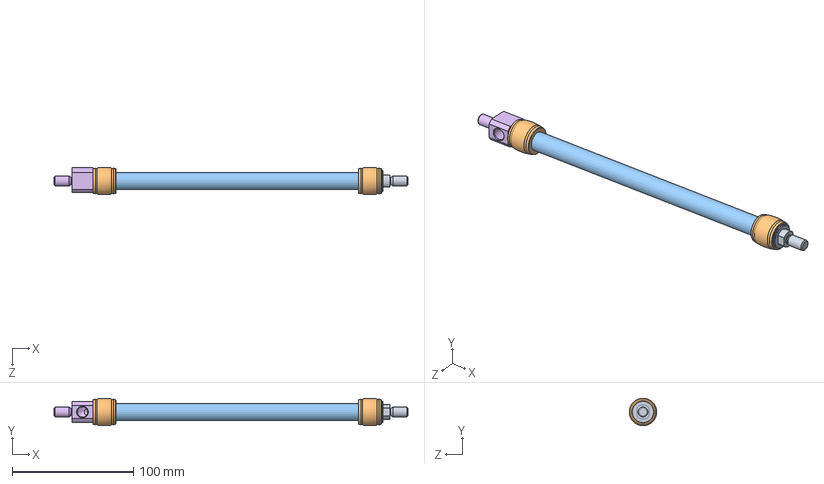
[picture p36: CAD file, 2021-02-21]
SPEAR_CAD/Part_Files/PAM/PAM.SLDASM
292.0 x 22.6 x 22.6 mm
surub
fiting x 2
membrana simpla - hds+hsj - parasolid
helix stanga jos - parasolid
helix dreapta sus - parasolid
surub cu alimentare

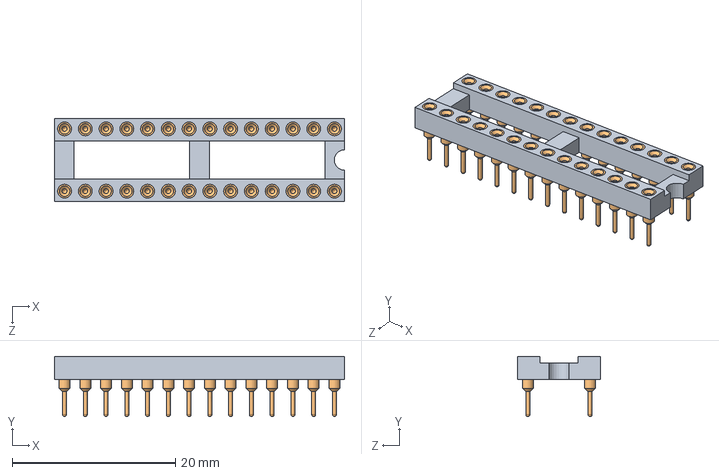
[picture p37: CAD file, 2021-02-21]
SPEAR_CAD/Part_Files/arduino-uno-r3-1.snapshot.3/arduino uno/dip28.SLDASM
35.5 x 7.37 x 10.1 mm
dip28
dip socket pin x 28

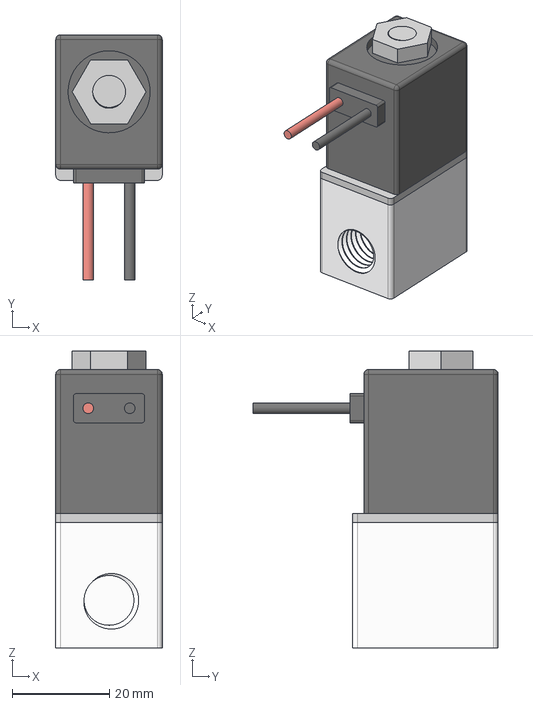
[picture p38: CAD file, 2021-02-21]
SPEAR_CAD/Part_Files/2v025-12v-solenoid-valve-1-4-1.snapshot.1/2V025 Solenoid Valve 12V.step
21.9 x 50.6 x 61.2 mm
Wires
Main Body

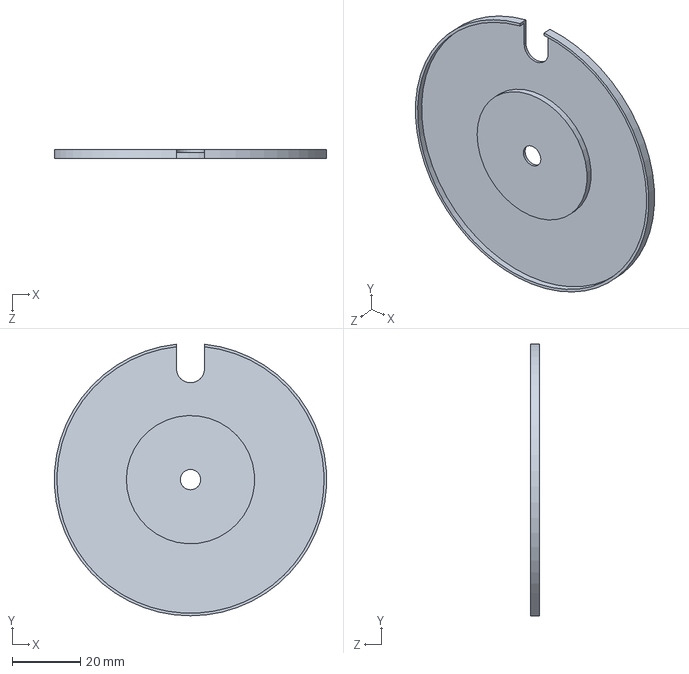
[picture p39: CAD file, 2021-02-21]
SPEAR_CAD/Part_Files/a-ratchet-hinge-for-knee-elbow-orthotics-1.snapshot.6/brace hinge/cover.SLDPRT
79.9 x 79.8 x 2.54 mm

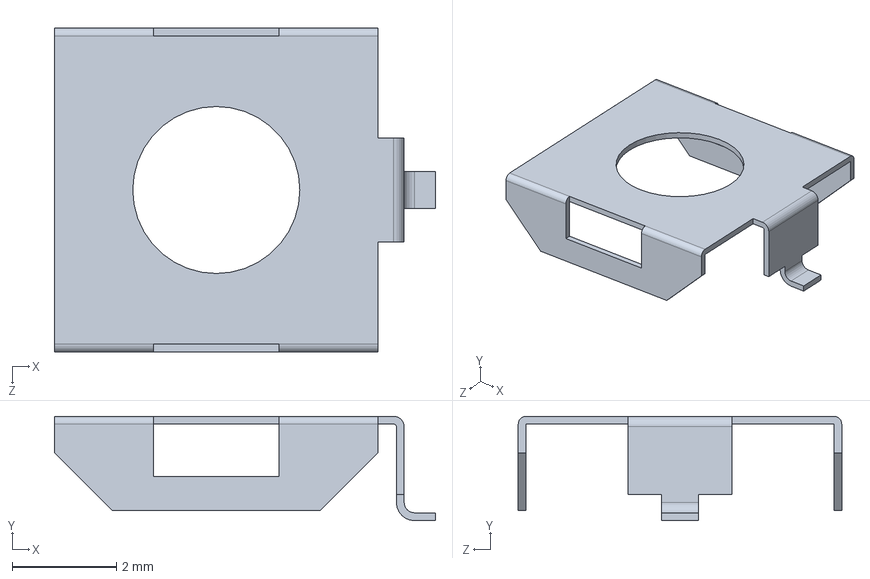
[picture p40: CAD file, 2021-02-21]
SPEAR_CAD/Part_Files/arduino-uno-r3-1.snapshot.3/arduino uno/RESET.SLDPRT
7.30 x 2.00 x 6.20 mm

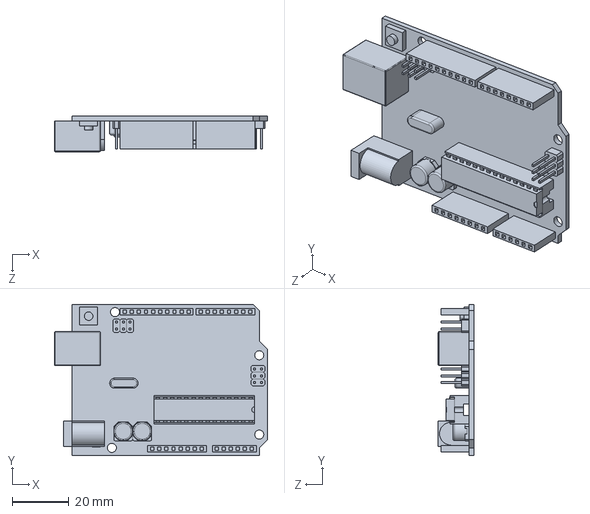
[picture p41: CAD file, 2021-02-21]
SPEAR_CAD/Part_Files/arduino-uno-with-solidworks-1.snapshot.1/arduino.SLDPRT
75.0 x 53.3 x 12.5 mm

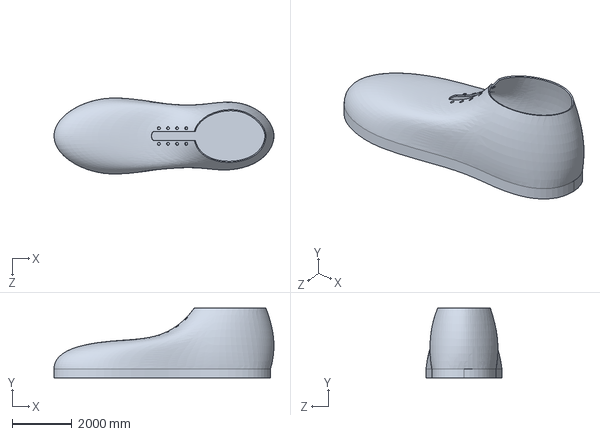
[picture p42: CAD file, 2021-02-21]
SPEAR_CAD/Part_Files/formal-cum-casual-shoe-1.snapshot.2/shoe.SLDPRT
7353.3 x 2336.8 x 2538.4 mm

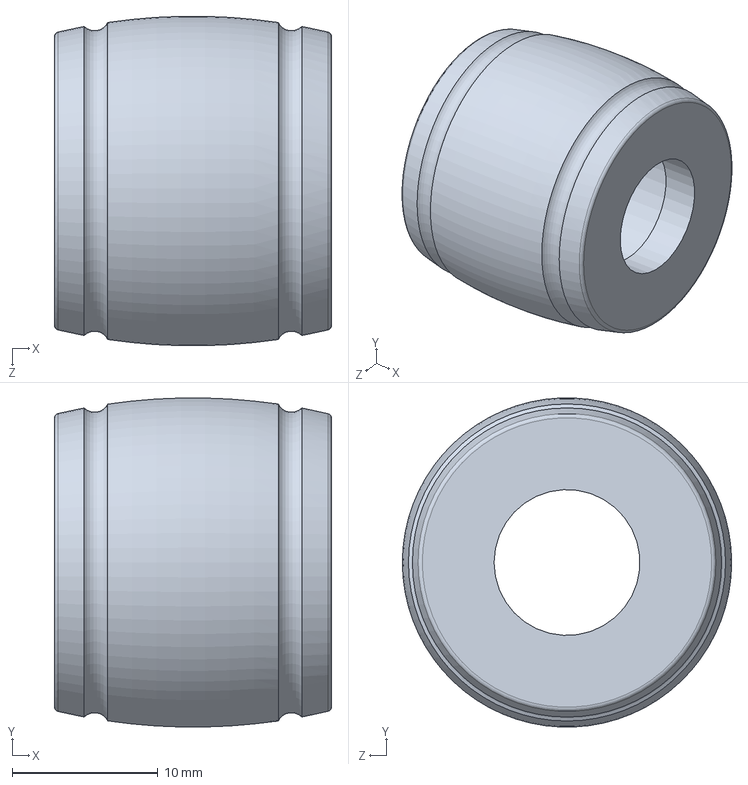
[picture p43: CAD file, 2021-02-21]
SPEAR_CAD/Part_Files/PAM/fiting.SLDPRT
19.0 x 22.6 x 22.6 mm

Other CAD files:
SPEAR_CAD/Part_Files/arduino-uno-r3-1.snapshot.3/arduino II/arduino uno.SLDASM
SPEAR_CAD/Part_Files/arduino-uno-r3-1.snapshot.3/arduino uno/RESET BUTTON.SLDASM
SPEAR_CAD/Part_Files/arduino-uno-r3-1.snapshot.3/arduino II/dip28.SLDASM
SPEAR_CAD/Part_Files/arduino-uno-r3-1.snapshot.3/arduino uno/USB type b.SLDPRT.SLDASM
SPEAR_CAD/Part_Files/a-ratchet-hinge-for-knee-elbow-orthotics-1.snapshot.6/bracehinge.STEP
SPEAR_CAD/Part_Files/2v025-12v-solenoid-valve-1-4-1.snapshot.1/2V025 Solenoid Valve 12V.f3d
SPEAR_CAD/Part_Files/2v025-12v-solenoid-valve-1-4-1.snapshot.1/2V025 Solenoid Valve 12V.iges
SPEAR_CAD/Part_Files/PAM/helix dreapta sus - parasolid.SLDPRT
SPEAR_CAD/Part_Files/PAM/helix stanga jos - parasolid .SLDPRT
SPEAR_CAD/Part_Files/PAM/membrana simpla - hds+hsj - parasolid.SLDPRT
SPEAR_CAD/Part_Files/PAM/surub cu alimentare.SLDPRT
SPEAR_CAD/Part_Files/PAM/surub.SLDPRT
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
